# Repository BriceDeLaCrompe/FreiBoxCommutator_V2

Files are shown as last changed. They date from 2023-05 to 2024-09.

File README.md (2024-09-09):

# FreiBoxCommutator_V2

We redesigned the 3D-printed FreiBox commutator to simplify assembly and reduce noise. The 3D-printed gears have been replaced with a timing pulley system.

Since the detection principle and Arduino code are the same as in v1, please refer to our previous version on GitHub. Don't forget to cite our paper:
- https://github.com/Optophys-Lab/FreiBox/tree/main/Commutator_FreiBox2022
- FreiBox: A Versatile Open-Source Behavioral Setup for Investigating the Neuronal Correlates of Behavioral Flexibility via 1-Photon Imaging in Freely Moving Mice
Brice De La Crompe, Megan Schneck, Florian Steenbergen, Artur Schneider, Ilka Diester
eNeuro 27 April 2023, 10 (4) ENEURO.0469-22.2023; DOI: 10.1523/ENEURO.0469-22.2023

/!\ Assembly Instructions: Before assembling the commutator, please check the file "FreiBoxCommutator_V2_AssemblyInstruction.pptx."

Feel free to share any ideas for improving the design! I would appreciate your feedback.

Note regarding the electronic circuit:
If you prefer not to solder the electronic circuit yourself, you can use a motor driver shield directly.

Brice.



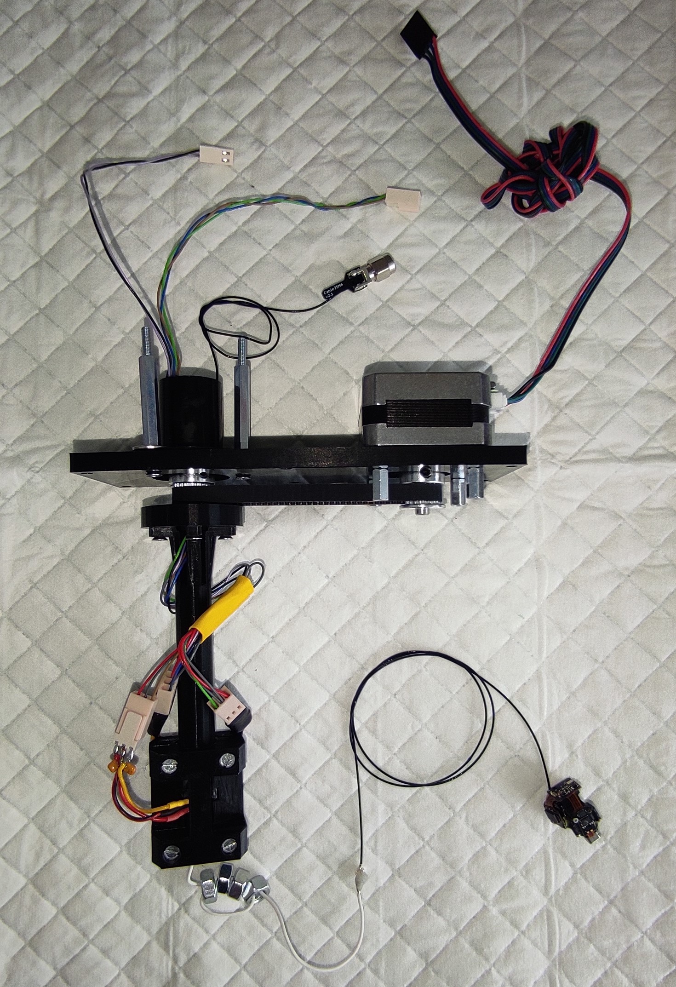
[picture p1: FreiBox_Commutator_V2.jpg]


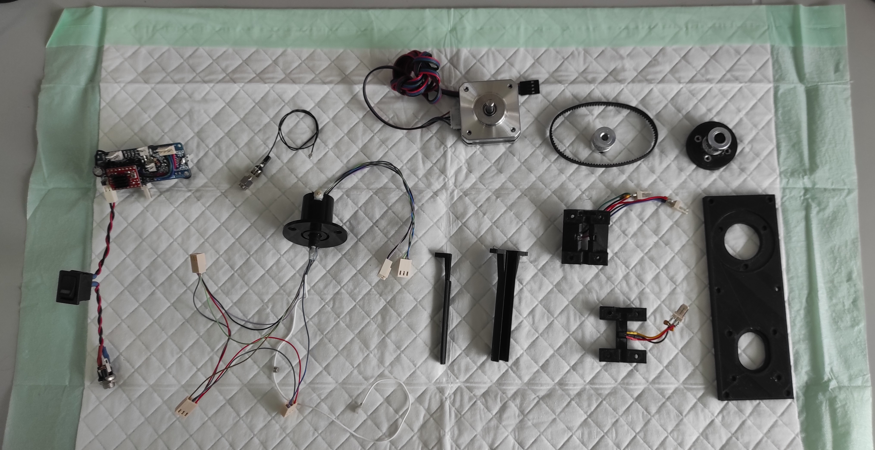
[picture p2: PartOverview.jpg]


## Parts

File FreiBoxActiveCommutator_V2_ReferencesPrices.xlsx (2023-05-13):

ID | Product | Provider/ Ref | Quantity | Price (in €) | Total (in €) | Total Per Unit (in €) | Link
1 | Nema17-03 step motor - 0.2 Nm - 1.2 A | Conrad / 2148831 - 62 | 1 | 12.99 | 12.99 | 12.99 | https://www.conrad.de/de/p/joy-it-schrittmotor-nema17-03-nema17-03-0-2-nm-1-2-a-wellen-durchmesser-5-mm-2148831.html
2 | Slip ring - 12 wires - 22mm diameter | Digikey / 1528-1176-ND | 1 | 21.54 | 21.54 | 21.54 | https://www.digikey.de/en/products/detail/adafruit-industries-llc/1196/5353636?s=N4IgTCBcDaIAQEYCsYAcBaBCDsA2dAcgCIgC6AvkA
3 | GT2 Timing Pulley - 5mm Bore - 6mm Belt - 20 Tooth (Pack of 10) | Amazon | 1 | 12.99 | 12.99 | 1.299 | https://www.amazon.de/gp/product/B07K79D985/ref=ppx_yo_dt_b_asin_title_o01_s02?ie=UTF8&psc=1
4 | GT2 Timing Pulley - 8mm Bore - 6mm Belt - 20 Tooth (Pack of 10) | Amazon | 1 | 12.17 | 12.17 | 1.217 | https://www.amazon.de/gp/product/B07D92S592/ref=ppx_yo_dt_b_asin_title_o00_s00?ie=UTF8&th=1
5 | Closed Timing Belt - 200 mm Length - 6 mm Belt (Pack of 2) | Amazon | 1 | 8.99 | 8.99 | 4.495 | https://www.amazon.de/gp/product/B07D92S592/ref=ppx_yo_dt_b_asin_title_o00_s00?ie=UTF8&th=1
6 | U.FL Connector Male Receptacle, 50Ohm, Surface Mount | Digikey / U.FL-R-SMT-1(01) | 2 | 1.38 | 2.76 | 2.76 | https://www.digikey.de/de/products/detail/hirose-electric-co-ltd/U-FL-R-SMT-1-01/3978494
7 | Hall sensor | Digikey / HAL830UT-A | 3 | 3.83 | 11.49 | 11.49 | https://www.digikey.de/en/products/detail/tdk-micronas-gmbh/HAL830UT-A/5271771
8 | Ceramic capacitor 100nF | Conrad / 1420294 | 10 | 0.1 | 1 | 1 | https://www.conrad.de/de/p/kemet-c320c104m5u5ta-keramik-kondensator-radial-bedrahtet-100-nf-50-v-20-l-x-b-x-h-5-08-x-3-18-x-5-84-mm-1-st-1420294.html?searchTy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
9 | Socket Contact | Conrad / 733884 - 62 | 5 | 1.29 | 6.45 | 6.45 | https://www.conrad.de/de/p/bkl-electronic-crimpkontakt-polzahl-gesamt-1-072637-20-st-733884.html
10 | Pin strip, 2 contacts, 2.54 mm Contact spacing | Conrad / 1580975 - 62 | 10 | 0.25 | 2.5 | 2.5 | https://www.conrad.de/de/p/tru-components-stiftleiste-standard-polzahl-gesamt-2-rastermass-2-54-mm-1580975-1-st-1580975.html
11 | Pin strip, 3 contacts, 2.54 mm Contact spacing | Conrad / 1580976 - 62 | 10 | 0.28 | 2.8 | 2.8 | https://www.conrad.de/de/p/tru-components-stiftleiste-standard-polzahl-gesamt-3-rastermass-2-54-mm-1580976-1-st-1580976.html
12 | Pin strip, 4 contacts, 2.54 mm Contact spacing | Conrad / 1580977 - 62 | 10 | 0.42 | 4.2 | 4.2 | https://www.conrad.de/de/p/tru-components-stiftleiste-standard-polzahl-gesamt-4-rastermass-2-54-mm-1580977-1-st-1580977.html
13 | Socket enclosure, 2 contacts, 2.54 mm Contact spacing | Conrad / 734021 | 10 | 0.27 | 2.7 | 2.7 | https://www.conrad.de/de/p/bkl-electronic-buchsengehaeuse-kabel-polzahl-gesamt-2-rastermass-2-54-mm-072630-1-st-734021.html
14 | Socket enclosure, 3 contacts, 2.54 mm Contact spacing | Conrad / 734036 - 62 | 10 | 0.28 | 2.8 | 2.8 | https://www.conrad.de/de/p/bkl-electronic-buchsengehaeuse-kabel-polzahl-gesamt-3-rastermass-2-54-mm-072631-1-st-734036.html
15 | Neodymium Magnet, 4mm diameter, 2mm thick (Pack of 50) | Amazon | 1 | 13.87 | 13.87 | 0.2774 | https://www.amazon.de/-/en/first4magnets-F042-N35-50-Diameter-Neodymium-Magnet/dp/B00TACMJEO?s=industrial&sbo=RZvfv%2F%2FHxDF%2BO5021pAnSA%3D%3D
16 | M3 nuts | Conrad / 132087 - 62 | 1 | 1.49 | 1.49 | 1.49 | https://www.conrad.de/de/p/toolcraft-132087-sechskantmuttern-m3-din-934-stahl-galvanisch-verzinkt-gelb-chromatisiert-100-st-132087.html
17 | M3 screws, 16mm length | Conrad / 522263 - 62 | 1 | 3.49 | 3.49 | 3.49 | https://www.conrad.de/de/p/toolcraft-m3-16-d965-4-8-a2k-194636-senkschrauben-m3-16-mm-schlitz-din-965-stahl-verzinkt-100-st-522263.html
18 | Epoxy glue, 2 components | Conrad / 478703 - 62 | 1 | 8.49 | 8.49 | 8.49 | https://www.conrad.de/de/p/uhu-plus-schnellfest-zwei-komponentenkleber-45700-35-g-478703.html
19 | Arduino Nano every | Conrad / 2240029 - 62 | 1 | 14.99 | 14.99 | 14.99 | https://www.conrad.de/de/p/arduino-abx00028-board-nano-every-nano-2240029.html
20 | A4988 stepper motor driver module (Pack of 5) | Amazon | 1 | 8.79 | 8.79 | 1.758 | https://www.amazon.de/-/en/pieces-stepper-driver-printer-controller/dp/B096XM7J4Z?s=industrial
21 | MKR Proto Shield | Conrad / TSX00001 | 1 | 12.99 | 12.99 | 12.99 | https://www.conrad.de/de/p/arduino-tsx00001-shield-1-st-1969863.html?searchType=SearchRedirect
22 | Electrolytic capacitor 100µF | Conrad / 1590477 | 1 | 0.12 | 0.12 | 0.12 | https://www.conrad.de/de/p/teapo-ksh107m063s1a5g15k-elektrolyt-kondensator-radial-bedrahtet-3-5-mm-100-f-63-v-20-x-h-8-mm-x-15-mm-1-st-1590477.html?searchType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
23 | Power Supply | Conrad / 1496993 - 62 | 1 | 7.49 | 7.49 | 7.49 | https://www.conrad.de/de/p/hycell-1201-0006-steckernetzteil-einstellbar-3-v-dc-4-5-v-dc-5-v-dc-6-v-dc-7-5-v-dc-9-v-dc-12-v-dc-600-ma-7-2-w-1496993.html?search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
24 | Low power connector socket | Conrad / 1582328 | 1 | 1.09 | 1.09 | 1.09 | https://www.conrad.com/p/tru-components-low-power-connector-socket-vertical-vertical-55-mm-25-mm-1-pcs-1582328
25 | Power toggle switch | Conrad / 1587515 | 1 | 1.79 | 1.79 | 1.79 | https://www.conrad.com/p/tru-components-toggle-switch-tc-r13-66a-02-250-v-ac-6-a-1-x-offon-latch-1-pcs-1587515
 |  |  |  | TOTAL (in €) | 179.98 | 132.2164
 |  |  |  |  |  |  |  | 0

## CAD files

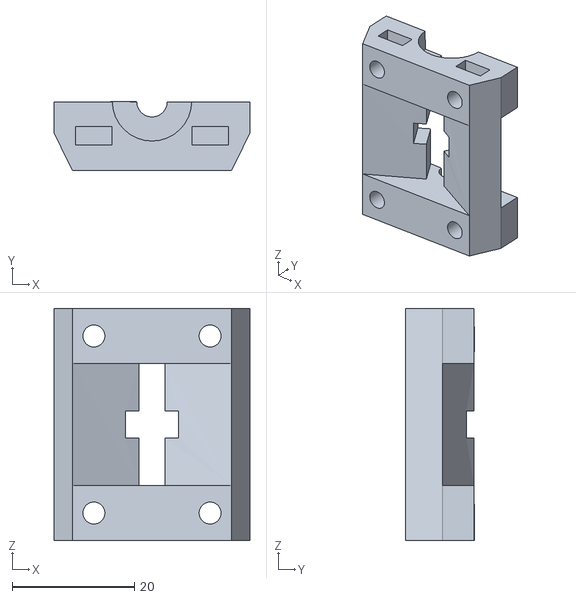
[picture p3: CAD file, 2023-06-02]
STLfiles/FreiBoxActiveCommutator_V2_Detector_Part1.stl
32.1 x 11.2 x 38.0

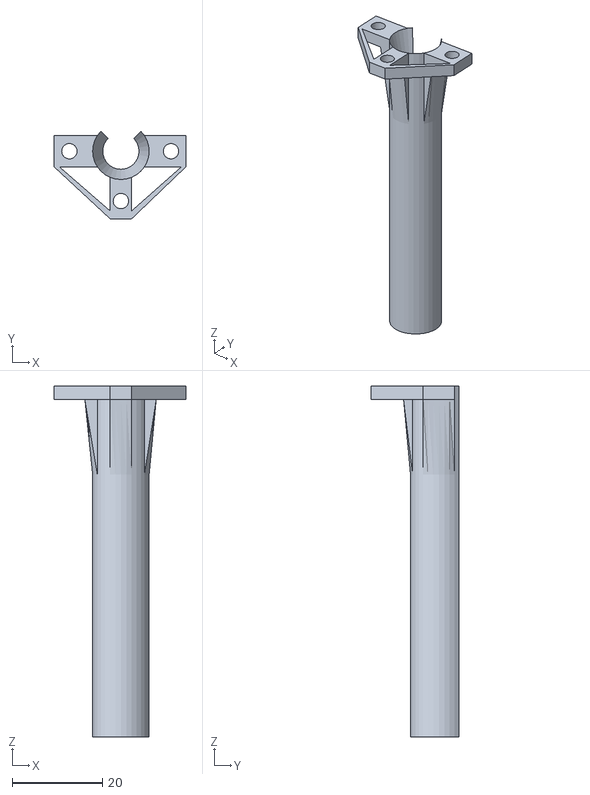
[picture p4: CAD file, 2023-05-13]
STLfiles/FreiBoxActiveCommutator_V2_Linker_Part1.stl
29.1 x 19.4 x 77.6

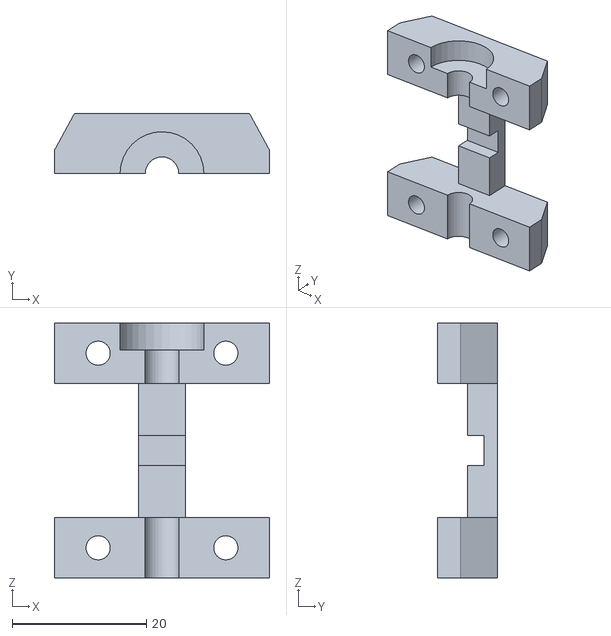
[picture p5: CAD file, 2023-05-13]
STLfiles/FreiBoxActiveCommutator_V2_Detector_Part2.stl
32.1 x 8.99 x 38.0

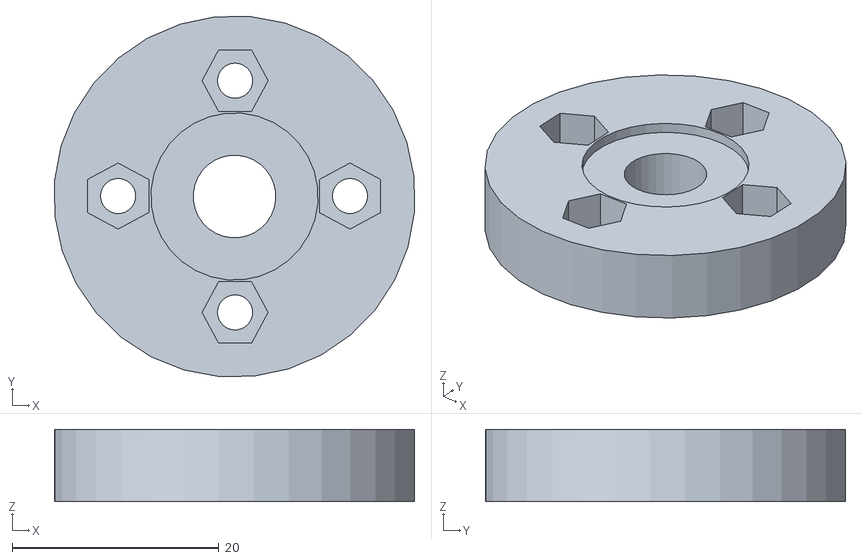
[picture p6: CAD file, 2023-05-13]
STLfiles/FreiBoxActiveCommutator_V2_PulleyLinker.stl
34.9 x 34.9 x 7.00

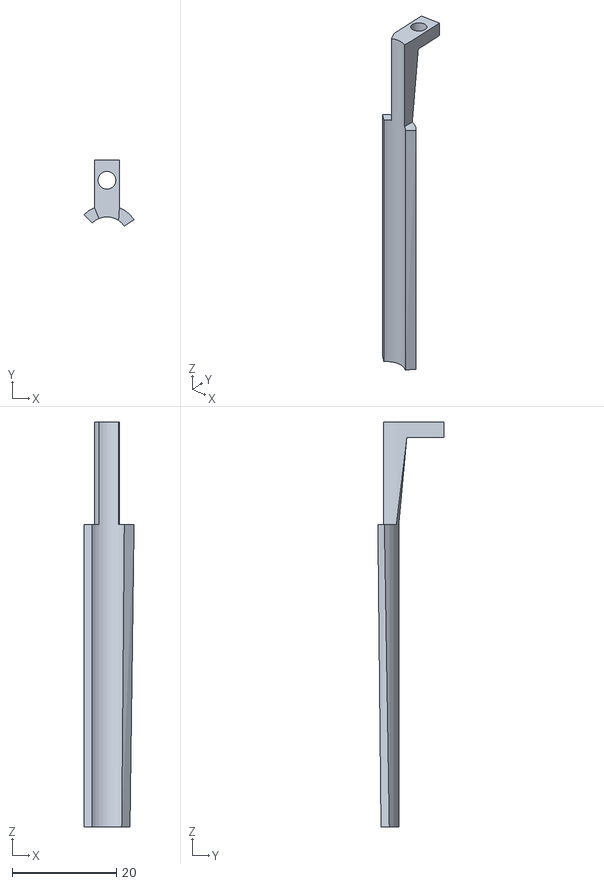
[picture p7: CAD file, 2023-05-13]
STLfiles/FreiBoxActiveCommutator_V2_Linker_Part2.stl
9.62 x 12.7 x 77.6

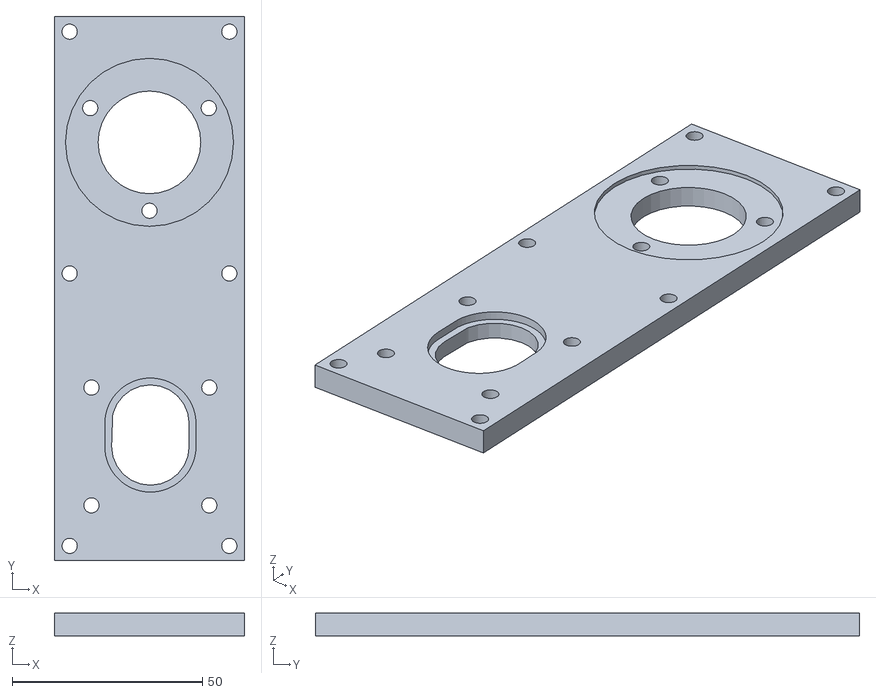
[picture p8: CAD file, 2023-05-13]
STLfiles/FreiBoxActiveCommutator_V2_CommutatorBase.stl
50.0 x 143.1 x 6.00

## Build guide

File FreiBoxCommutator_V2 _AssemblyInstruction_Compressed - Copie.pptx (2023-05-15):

## Assembly instruction

## FreiBox Active Commutator V2: Overview

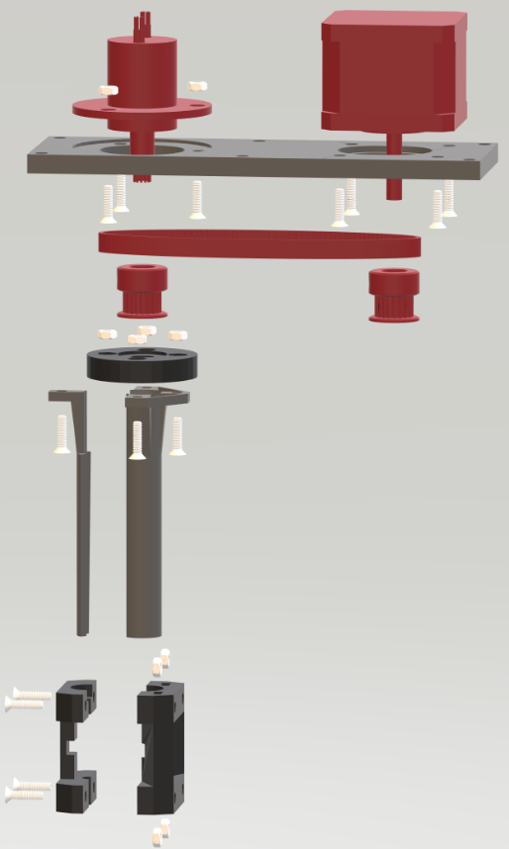
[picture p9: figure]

2

STL files

1

CommutatorBase

5

4

3

Component list

PulleyLinker

Linker_Part1

Linker_Part2

Detector_Part1

Detector _Part2

## Instruction overview

- Before sssembling the commutator, please read below!!
- Print, collect all the parts and build the electronic circuit
- Before final assembly, you must first build:
  - The pulley linker part (nuts insertion + pulley gluing)
  - The ring detector (capacitor and connector to be soldered to the hall sensor + gluing to the Detector _Part1 and Part2)
  - Solder the 2x U.FL (male) connectors to the slip ring and the miniscope cable end. Secure them with cement or epoxy.
  - Solder the miniscope cable to the slip ring
- Once the previous steps have been completed, you can assemble all the parts (except the Detector_Part2).
- After defining the position of the magnet, as well as the its polarity *, you can the superglue the magnet onto the miniscope cable. The magnet must be placed in the center of the hall detector centers.
/!\ *To avoid an inversion of the logic detection, the magnet polarity must to be checked first! The magnet must to be glue on its ‘south’ while its ‘north’ side must face the hall sensors (to get a positive signal)
- Weight/Ballast the miniscope (or neuropixel) cable with M5/M6 nuts. This stabilizes the movement of the magnet without changing the weight on the mouse
- Connect your cable to the electronic circuit. Load the Arduino code and test it.
- You are ready to image!

## Collect all parts before the assembling

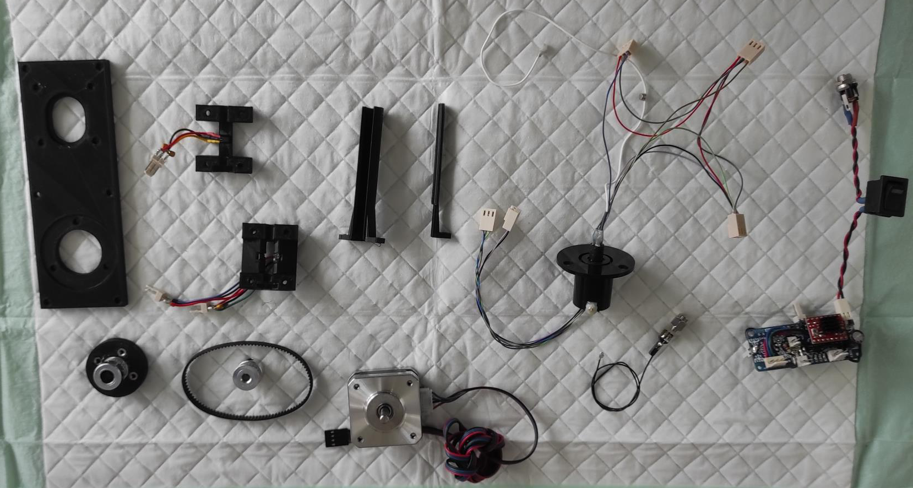
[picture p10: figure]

CommutatorBase

Assembled slip ring

Detector _Part2

Linker_Part1

Linker_Part2

Detector_Part1

Electronic
Circuit + Nano every

Nema
step motor

PulleyLinker

Timing pulley
And timing belt

U.FL (Female) to SMA cable
(to connect to the DAC)

## Assembling of the pulley linker

- First insert the M3 nut into the 4 corresponding slots of the linker pulley
- Then, glue the pulley linker to the with the GT2 timing pulley 8mm bore with epoxy. Avoid getting glue in the bore or in the nuts.

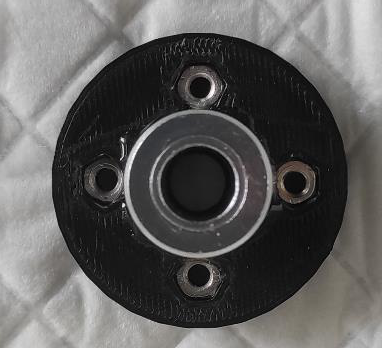
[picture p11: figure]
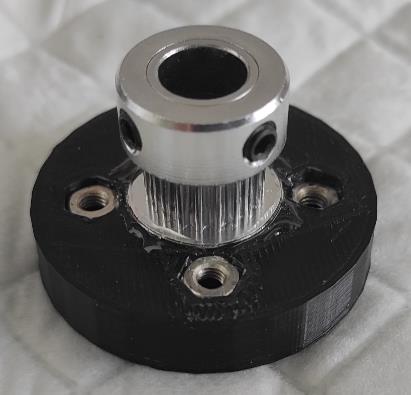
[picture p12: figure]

## The ring detector

1. Solder the capacitor to the hall sensor as shown
2. Stick the Hall sensor to the Ring Detector Part1 and Part2 with superglue
3. Using epoxy, glue the Detector_Part1 to the Linker_Part1
4. Insert the nuts into their corresponding slots (see arrows)

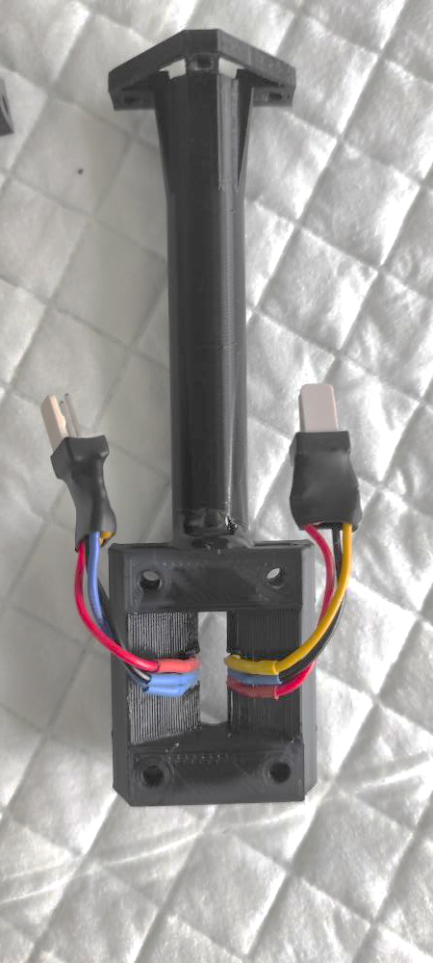
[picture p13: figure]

Epoxy

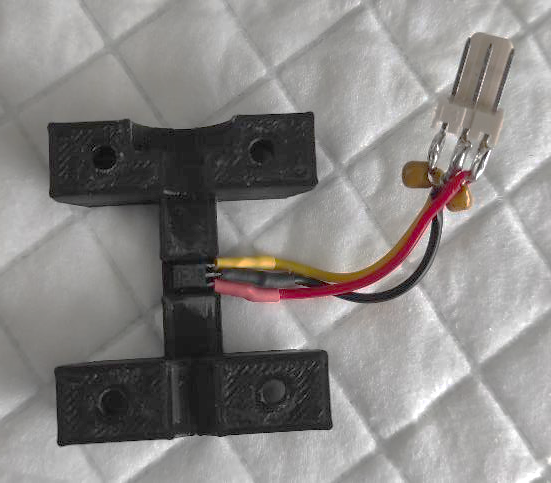
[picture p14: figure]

Signal/GND/5V

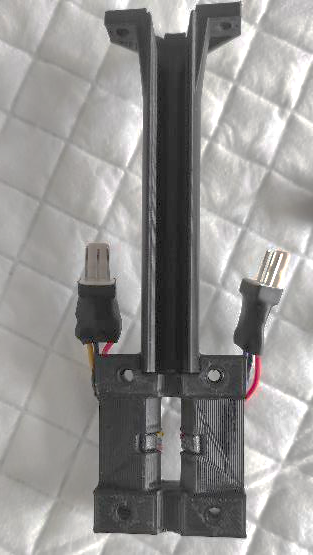
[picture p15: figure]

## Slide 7

Assembled slip ring

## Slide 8

Assembled slip ring

- The signals from the Miniscope (GND and 5V) and the Hall sensors (GND, 5V and the 3 analog signals from the hall sensors) are relayed via a slip ring and send to the Arduino.
- We decided to use the U.FL connector to keep the possibility of connecting another miniscope or changing a possible broken cable easily. However, we strongly advise avoiding repetitive connection/disconnection of the U.FL connectors. As for the miniscopes, they are a little fragile. Instead you should have a commutator for each miniscope/setup since the price is cheap !

Extended Data Figure 4-1
10.1523/ENEURO.0469-22.2023

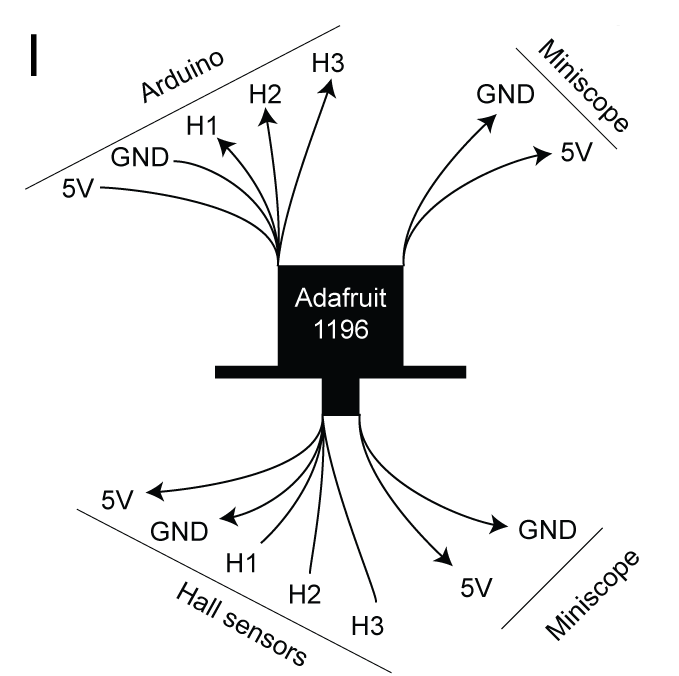
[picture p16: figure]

## Assembled slip ring

1. Miniscope cable soldering to slip ring
/!\ Minimize the length of the cable coming from the slip ring
2. U.FL soldering to Slip ring
3. U.FL soldering to miniscope cable
4. Check the connectivity !! A shortcut between the 2 miniscope cables can damage the DAQ!!!
5. Fixing with epoxy/cement
/!\ Minimize the Epoxy to ensure that the 8mm bore pulley linker is still fitting around the slip ring rotor (* on the photo).

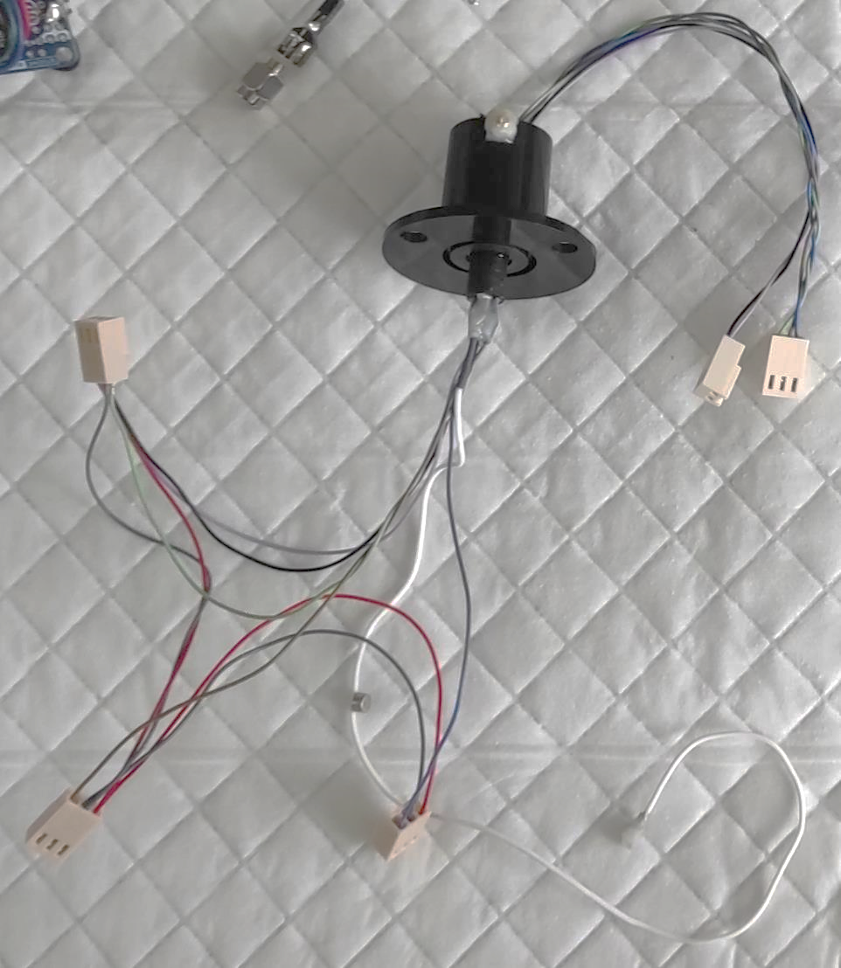
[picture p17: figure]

U.FL
(Male)

Connectors for the
3 hall sensors
(GND, 5v and signal)

*

<8mm

GND
and 5v

3 analogic
signals

4mm
magnet

U.FL
(Male)

Miniscope cable

## U.FL soldering to the Slip ring

GND

Signal

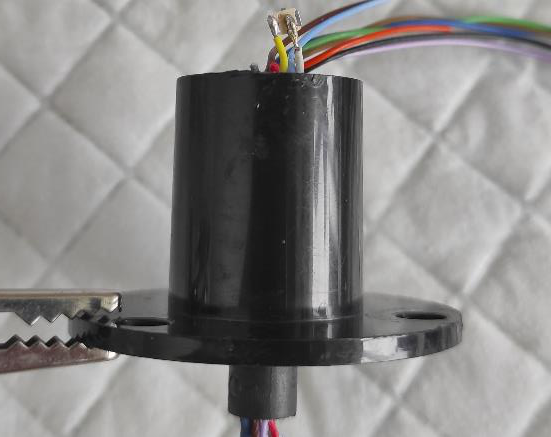
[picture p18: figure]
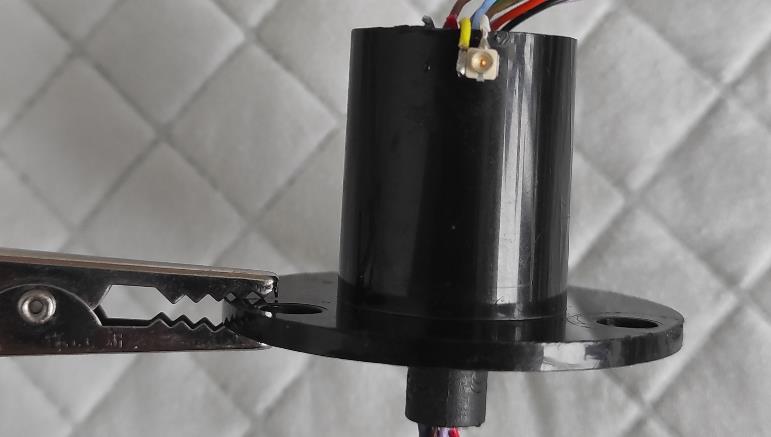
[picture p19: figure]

## After having testing the U.FL connectivity, secure the U.FL connector to the slip ring with Epoxy/Cement

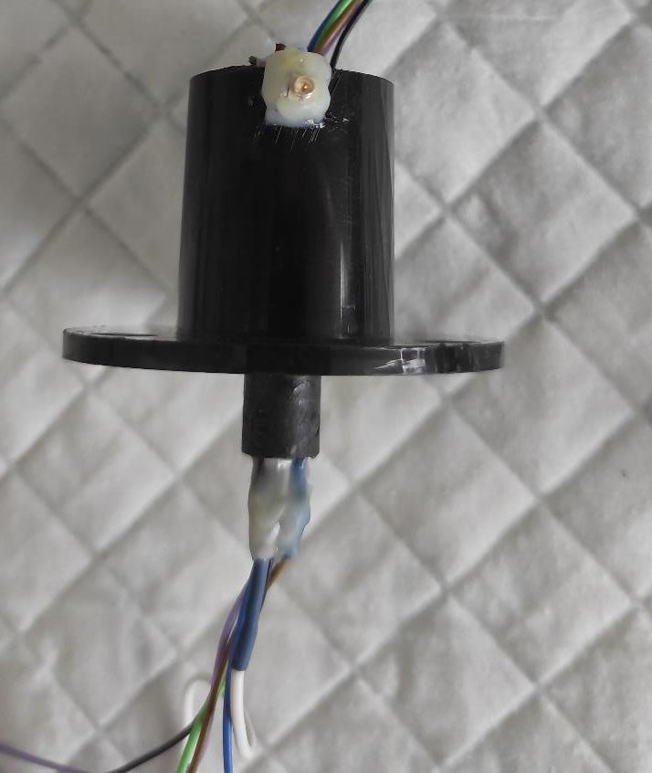
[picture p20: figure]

We also advice to glue the miniscope cable
with epoxy as shown

*

/!\ Minimize the Epoxy to ensure that the 8mm bore pulley linker is still fitting around the slip ring rotor (* on the photo).

<8mm

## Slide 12

Pre-assembling

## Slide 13

Pre-assembling

- Connect the timing pulleys to the slip ring and the motor
- Secure the slip ring, insert the timing belt and place the motor
- Insert Nuts in the Ring detector

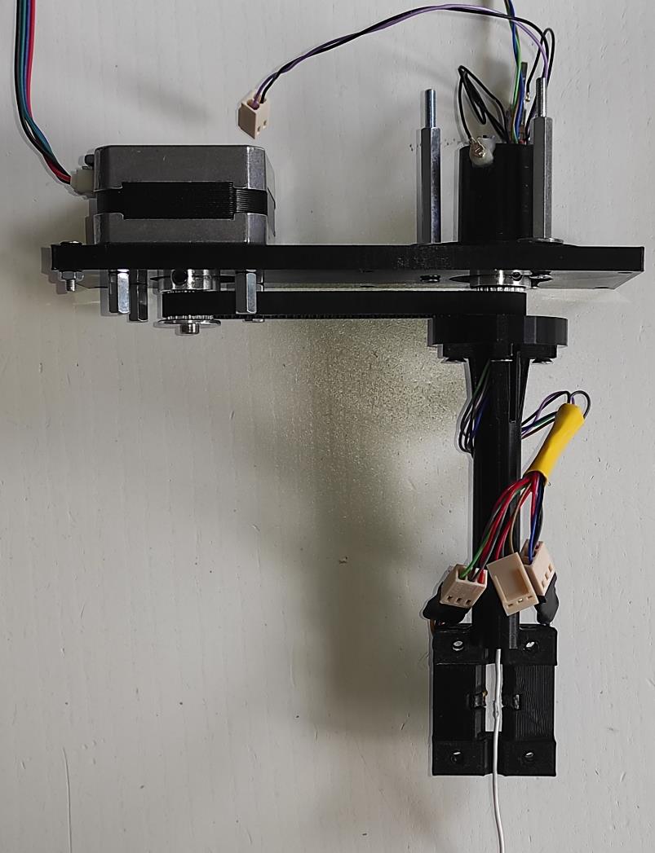
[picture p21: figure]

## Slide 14

Magnet positioning on the cable

1. Identify magnet orientation
2. Glue the magnet to the cable

## Identify the North/Pole pole

- Since the voltage output of the HAL830 Hall sensor is sensitive to the direction of the magnetic field (see on right figure), it is important to identify the orientation of the magnet before sticking it.
- To identify magnet orientation:
  - Connect a hall sensor to an Arduino(5v, Gnd and signal) and record its output signal
  - Mark one side of the magnet with a marker
  - Attached the Magnet to a screwdriver
  - Identify the magnet pole (see after)

North pole
Facing the hall sensor

Hall sensor analog signal

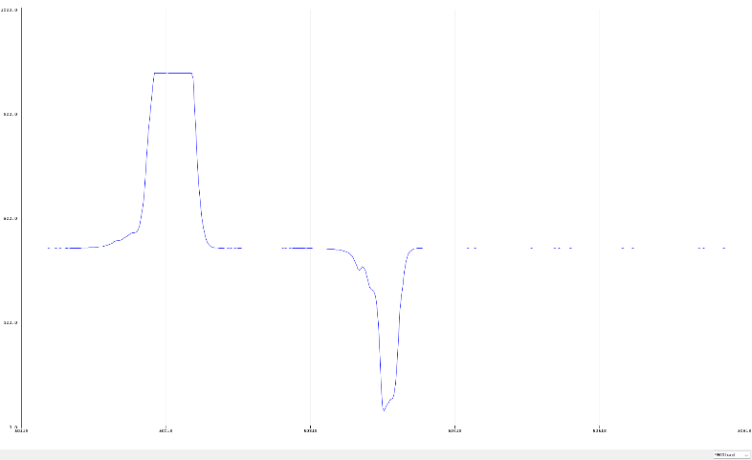
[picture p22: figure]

baseline

South pole
facing the hall sensor

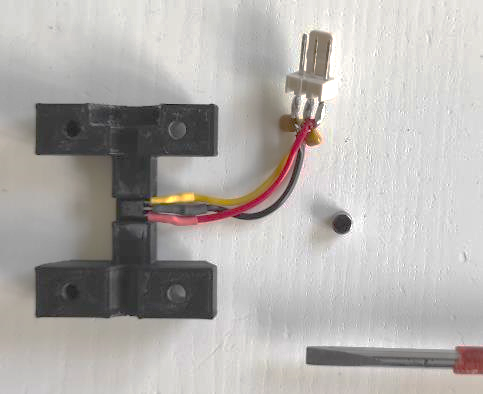
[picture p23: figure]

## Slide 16

Identify the North/Pole pole -2

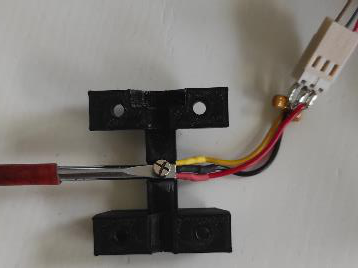
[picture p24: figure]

baseline

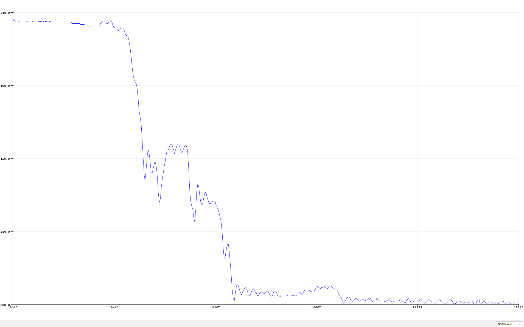
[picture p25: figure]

The unmarked side is the south

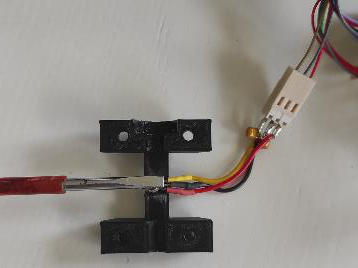
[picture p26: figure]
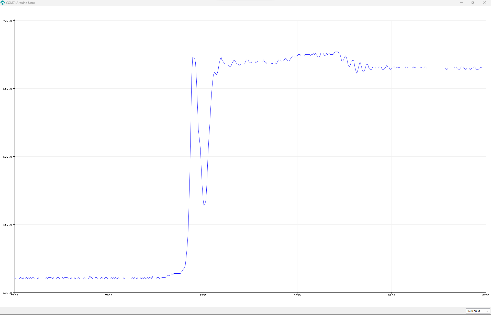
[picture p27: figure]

baseline

While the marked side is the north

## Magnet positioning on the cable

- Pull on the miniscope cable and mark it to identify the magnet position (red arrow)
- Glue the magnet and be sure that the north pole is facing the hall sensors during cable rotation (marked with a cross) :

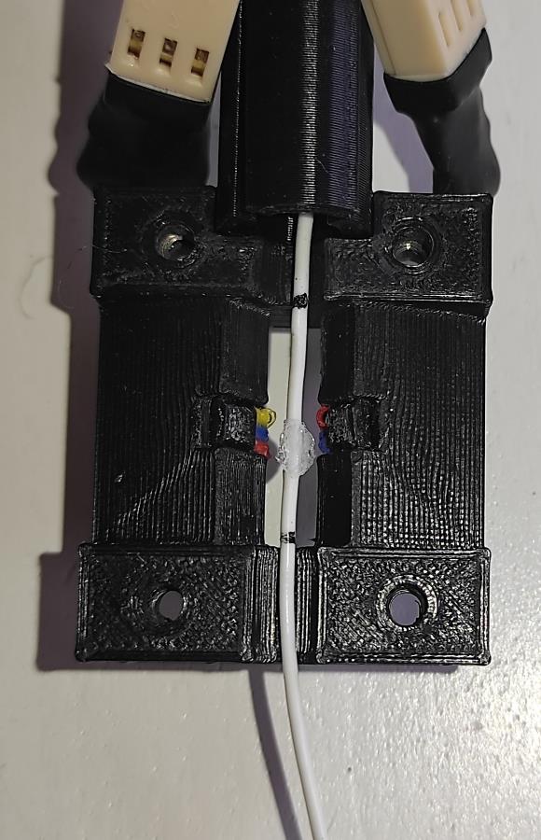
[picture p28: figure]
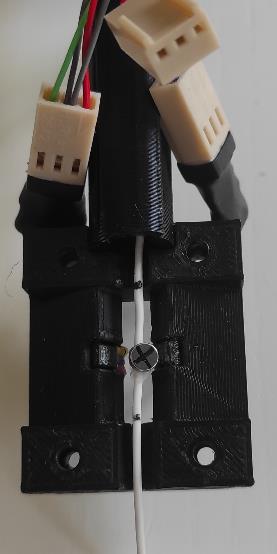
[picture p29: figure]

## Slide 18

Final assembly

## Final assembly

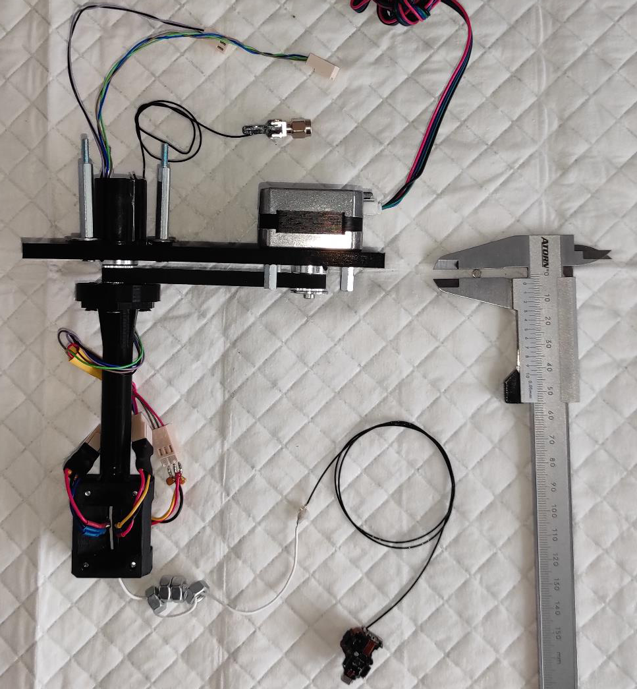
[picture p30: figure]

The nuts are used to ‘ballast’ the miniscope cable.
Particularly useful for other flexible cables such as the neuropixel cable

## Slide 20

Electronic circuit

## Electronic circuit

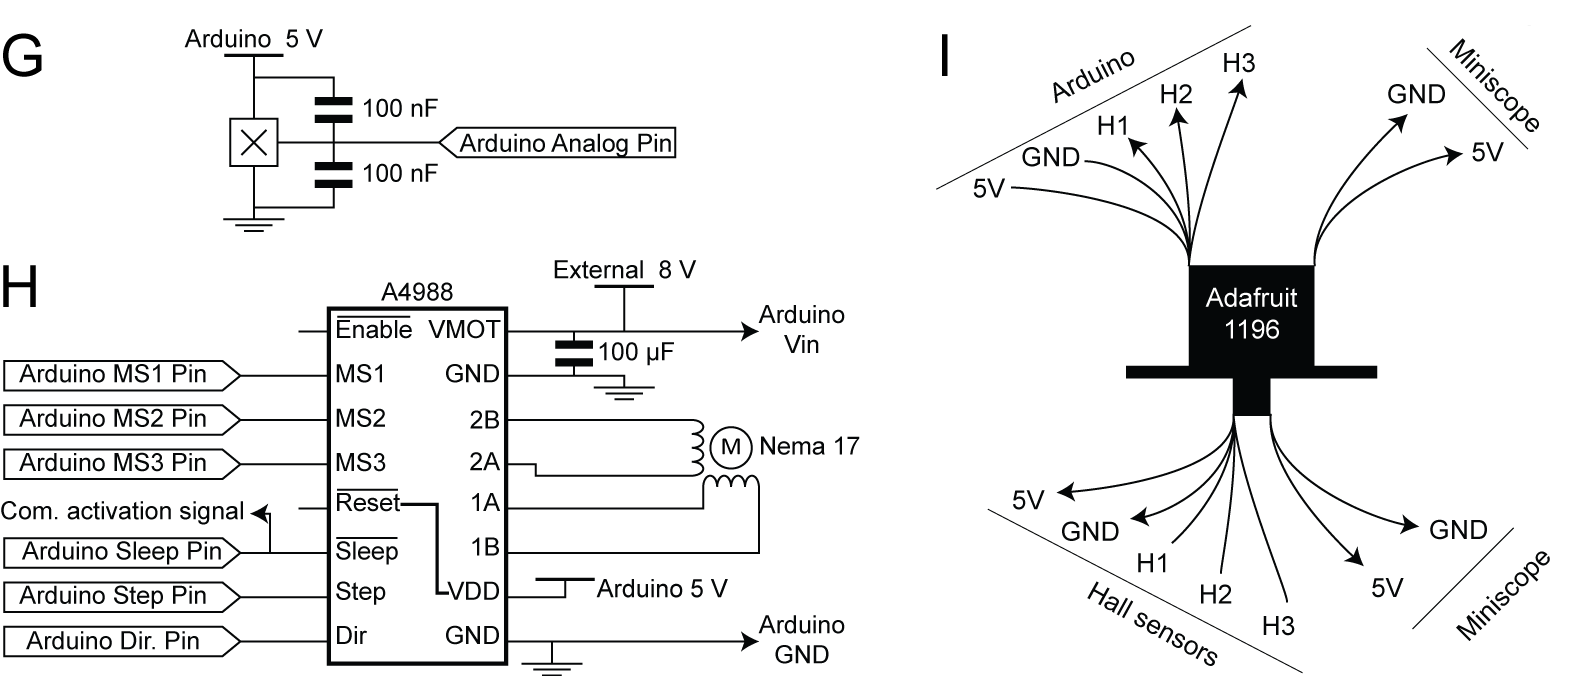
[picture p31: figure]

G–I, To build the FreiBox commutator, the 3 Hall sensors (G) and a motor driver card (H) are connected to the step motor and the Arduino; the signals from the Miniscope and the Hall sensors are relayed via a slip ring (I).

Extended Data Figure 4-1
10.1523/ENEURO.0469-22.2023

## Electronic circuit

- If you don’t want to solder the circuit yourself, you can use Arduino motor shield such as:
  - For Arduino Nano: Ks0152 keyestudio CNC Shield V4
  - For Arduino Uno or Mega: Joy-it ARD-CNC-Kit1 Motortreiber

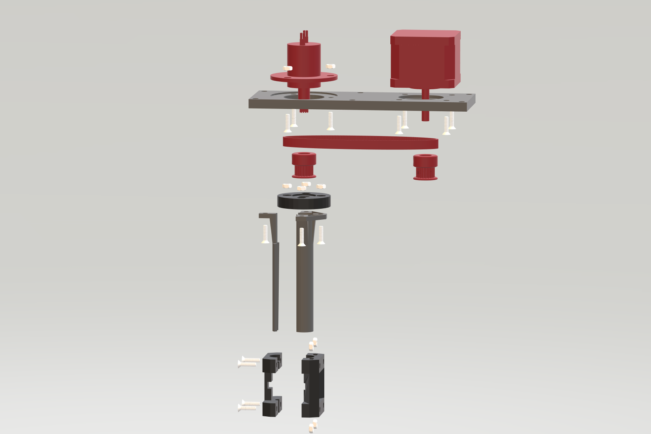
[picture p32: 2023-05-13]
FreiBoxActiveCommutator_V2_Assembly.tiff
